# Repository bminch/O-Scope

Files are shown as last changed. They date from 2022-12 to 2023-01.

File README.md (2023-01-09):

# O-Scope
This repository contains the PCB design files, firmware, and software for the O-Scope, which is a low-cost (i.e., a cut-tape BoM cost of about $30 
as of fall 2020) two-channel oscilloscope / single-channel waveform generator up to a bandwidth of 200 kHz that fits into a solderless breadboard.  The oscilloscope's vertical resolution is 12 bits and each channel is sampled at 4 MS/s.  Each channel has a sample buffer of 1,500 points.  The 
oscilloscope probes are differential and have an equivalent input impedance of 1 MΩ || 15 pF with two input voltage ranges: ±10V and ±2V.  The 
waveform generator is capable of producing DC, sinusoidal, square, and triangle waves with an adjustable offset in the range of 0 - 5V. For an overview 
and demonstration of the O-Scope, see https://youtu.be/0cz0oYtfNsY.

I designed this instrument during the summer of 2020 based on a prior prototype, which I had made during the summers of 2016 and 2017, in order to support 
a remote / hybrid offering of ENGR 1125: Introduction to Sensors, Instrumentation, and Measurement at Olin College during the spring of 2021 in the midst 
of the COVID-19 pandemic.  During October and November 2020, I hand assembled and calibrated 90 O-Scopes at home, as shown in https://youtu.be/zYawotioLMc.  We used these instruments successfully during the spring 2021 and spring 2022 offerings of the course at Olin.

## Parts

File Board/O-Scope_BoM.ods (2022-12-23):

 |  | Number of boards = | 100 | Parts cost / board = | $28.34 |  |  |  |  |  |  |  |  |  |  |  |  |  |  |  |  |  |  | 0
Item | Qty | Reference(s) | Item Description | Manfacurer # | Digikey # (Cut Tape) | Digikey Product Page | Breakpoint | Price | Breakpoint | Price | Breakpoint | Price | Breakpoint | Price | Breakpoint | Price | Breakpoint | Price | Breakpoint | Price | Breakpoint | Price | Breakpoint | Price | Qty / Board | Total Qty | Unit Cost | Extended Cost | Cost / Board
1 | 3 | C1, C7, C8 | 0805, ±10%, X5R, 25-V, 10-µF ceramic capacitor | CC0805KKX5R8BB106 | 311-1869-1-ND | https://www.digikey.com/product-detail/en/yageo/CC0805KKX5R8BB106/311-1869-1-ND/5195771 | 1 | $0.50 | 10 | $0.35 | 100 | $0.23 | 500 | $0.17 | 1000 | $0.15 |  |  |  |  |  |  |  |  | 3 | 300 | $0.23 | $69.24 | $0.69
2 | 16 | C2, C3, C4, C5, C6, C9, C27, C28, C29, C30, C31, C34, C36, C37, C39, C40 | 0603, ±10%, X7R, 50-V, 0.1-µF ceramic capacitor | CL10B104JB8NNNC | 1276-1033-1-ND | https://www.digikey.com/product-detail/en/samsung-electro-mechanics/CL10B104JB8NNNC/1276-1033-1-ND/3889119 | 1 | $0.10 | 10 | $0.05 | 100 | $0.02 | 500 | $0.02 | 1000 | $0.01 |  |  |  |  |  |  |  |  | 16 | 1600 | $0.01 | $19.36 | $0.19
3 | 5 | C10, C19, C20, C21, C22 | 0603, ±1%, NP0, 50-V, 100-pF ceramic capacitor | 06035A101FAT2A | 478-6202-1-ND | https://www.digikey.com/product-detail/en/avx-corporation/06035A101FAT2A/478-6202-1-ND/2391401 | 1 | $0.21 | 10 | $0.14 | 100 | $0.07 | 500 | $0.05 | 1000 | $0.04 |  |  |  |  |  |  |  |  | 5 | 500 | $0.05 | $24.51 | $0.25
4 | 4 | C11, C12, C13, C14 | 0603, ±1%, NP0, 250-V, 15-pF ceramic capacitor | CBR06C150FAGAC | 399-8784-1-ND | http://www.digikey.com/product-detail/en/kemet/CBR06C150FAGAC/399-8784-1-ND/3479731 | 1 | $0.85 | 10 | $0.63 | 100 | $0.43 | 500 | $0.34 | 1000 | $0.29 |  |  |  |  |  |  |  |  | 4 | 400 | $0.43 | $171.36 | $1.71
5 | 4 | C15, C16, C17, C18 | 0603, ±1%, NP0, 50-V, 1-nF ceramic capacitor | GRM1885C1H102FA01D | 490-6376-1-ND | http://www.digikey.com/product-detail/en/murata-electronics-north-america/GRM1885C1H102FA01D/490-6376-1-ND/3845573 | 1 | $0.21 | 10 | $0.15 | 100 | $0.07 | 500 | $0.05 | 1000 | $0.04 |  |  |  |  |  |  |  |  | 4 | 400 | $0.07 | $27.52 | $0.28
6 | 4 | C23, C24, C25, C26 | SGC3S300NM 8.0 - 30-pF, 500-V trimmer capacitor | SGC3S300NM | 2447-SGC3S300NMCT-ND | https://www.digikey.com/product-detail/en/ew-electronics/SGC3S300NM/2447-SGC3S300NMCT-ND/11689325 | 1 | $0.96 | 10 | $0.84 | 25 | $0.79 | 50 | $0.76 | 100 | $0.73 | 250 | $0.66 | 500 | $0.59 |  |  |  |  | 4 | 400 | $0.66 | $264.00 | $2.64
7 | 1 | C35 | 0603, ±5%, X7R, 50-V, 10-nF ceramic capacitor | C0603C103J5RACTU | 399-1092-1-ND | https://www.digikey.com/product-search/en?keywords=399-1092-1-ND | 1 | $0.10 | 10 | $0.05 | 100 | $0.02 | 500 | $0.02 | 1000 | $0.01 |  |  |  |  |  |  |  |  | 1 | 100 | $0.02 | $2.36 | $0.02
8 | 1 | C38 | 0603, X7R, 25-V, 1-µF capacitor | CL10B105KA8NNNC | 1276-1184-1-ND | https://www.digikey.com/product-detail/en/samsung-electro-mechanics/CL10B105KA8NNNC/1276-1184-1-ND/3889270 | 1 | $0.10 | 10 | $0.05 | 100 | $0.02 | 500 | $0.02 | 1000 | $0.01 |  |  |  |  |  |  |  |  | 1 | 100 | $0.02 | $2.42 | $0.02
9 | 2 | D1, D4 | 0805 green LED | LTST-C170TGKT | 160-1887-1-ND | http://www.digikey.com/product-search/en?keywords=160-1887-1-ND | 1 | $0.59 | 10 | $0.43 | 100 | $0.28 | 500 | $0.20 | 1000 | $0.16 |  |  |  |  |  |  |  |  | 2 | 200 | $0.28 | $55.74 | $0.56
10 | 1 | D2 | 0805 red LED | LTST-C171KRKT | 160-1427-1-ND | http://www.digikey.com/product-search/en?keywords=160-1427-1-ND | 1 | $0.28 | 10 | $0.20 | 100 | $0.10 | 500 | $0.06 | 1000 | $0.05 |  |  |  |  |  |  |  |  | 1 | 100 | $0.10 | $9.68 | $0.10
11 | 1 | D3 | 0805 blue LED | LTST-C170TBKT | 160-1579-1-ND | http://www.digikey.com/product-search/en?keywords=160-1579-1-ND | 1 | $0.39 | 10 | $0.28 | 100 | $0.16 | 500 | $0.11 | 1000 | $0.09 |  |  |  |  |  |  |  |  | 1 | 100 | $0.16 | $16.07 | $0.16
12 | 1 | J2 | USB micro-B connector, SMT, right angle, horizontal | 2040002-1 | A108263CT-ND | http://www.digikey.com/product-detail/en/te-connectivity-amp-connectors/2040002-1/A108263CT-ND/4021990 | 1 | $2.23 | 10 | $2.03 | 25 | $1.90 | 50 | $1.82 | 100 | $1.74 | 250 | $1.57 | 500 | $1.45 |  |  |  |  | 1 | 100 | $1.74 | $173.71 | $1.74
13 | 2 | J3, J4 | 1x06, 0.1-in vertical male pin header | PBC36SAAN | S1011E-36-ND | https://www.digikey.com/product-detail/en/sullins-connector-solutions/PBC36SAAN/S1011E-36-ND/859621 | 1 | $2.10 | 10 | $1.88 | 100 | $1.55 | 500 | $1.23 | 1000 | $1.07 |  |  |  |  |  |  |  |  | 0.33 | 34 | $1.88 | $63.99 | $0.64
14 | 2 | J5, J6 | 1x02, 0.1-in vertical male pin header | PBC36SAAN | S1011E-36-ND | https://www.digikey.com/product-detail/en/sullins-connector-solutions/PBC36SAAN/S1011E-36-ND/859621 | 1 | $2.10 | 10 | $1.88 | 100 | $1.55 | 500 | $1.23 | 1000 | $1.07 |  |  |  |  |  |  |  |  | 0.11 | 12 | $1.88 | $22.58 | $0.23
15 | 4 | R1, R2, R37, R39 | 0603, ±1%, ±100ppm/Cº, 1/10-W, 10-kΩ resistor | RC0603FR-0710KL | 311-10.0KHRCT-ND | https://www.digikey.com/product-search/en?keywords=311-10.0KHRCT-ND | 1 | $0.10 | 10 | $0.02 | 100 | $0.01 | 1000 | $0.00 | 2500 | $0.00 |  |  |  |  |  |  |  |  | 4 | 400 | $0.01 | $3.76 | $0.04
16 | 4 | R4, R5, R6, R7 | 0603, ±1%, ±100ppm/Cº, 1/10-W, 1-kΩ resistor | RC0603FR-071KL | 311-1.00KHRCT-ND | http://www.digikey.com/product-search/en?keywords=311-1.00KHRCT-ND | 1 | $0.10 | 10 | $0.02 | 100 | $0.01 | 1000 | $0.00 | 2500 | $0.00 |  |  |  |  |  |  |  |  | 4 | 400 | $0.01 | $3.76 | $0.04
17 | 2 | R26, R28 | 0603, ±1%, ±100ppm/ºC, 1/10-W, 806-Ω resistor | RC0603FR-07806RL | 311-806HRCT-ND | https://www.digikey.com/products/en?keywords=311-806HRCT-ND | 1 | $0.10 | 10 | $0.02 | 100 | $0.01 | 1000 | $0.00 | 2500 | $0.00 |  |  |  |  |  |  |  |  | 2 | 200 | $0.01 | $1.88 | $0.02
18 | 4 | R8, R9, R10, R11 | 0805, ±1%, ±100ppm/ºC, 1/8-W, 887-kΩ resistor | CRCW0805887KFKEA | 541-887KCCT-ND | https://www.digikey.com/products/en?keywords=541-887KCCT-ND | 1 | $0.10 | 10 | $0.06 | 100 | $0.03 | 1000 | $0.01 | 2500 | $0.01 |  |  |  |  |  |  |  |  | 4 | 400 | $0.03 | $10.16 | $0.10
19 | 10 | R12, R13, R14, R15, R16, R21, R46, R47, R49, R50 | 0603, ±1%, ±100ppm/ºC, 1/10-W, 13-kΩ resistor | RC0603FR-0713KL | 311-13.0KHRCT-ND | https://www.digikey.com/products/en?keywords=311-13.0KHRCT-ND | 1 | $0.10 | 10 | $0.02 | 100 | $0.01 | 1000 | $0.00 | 2500 | $0.00 |  |  |  |  |  |  |  |  | 10 | 1000 | $0.00 | $4.21 | $0.04
20 | 8 | R17, R18, R19, R20, R22, R23, R24, R25 | 0603, ±1%, ±100ppm/ºC, 1/10-W, 200-kΩ resistor | RC0603FR-07200KL | 311-200KHRCT-ND | https://www.digikey.com/products/en?keywords=311-200KHRCT-ND | 1 | $0.10 | 10 | $0.02 | 100 | $0.01 | 1000 | $0.00 | 2500 | $0.00 |  |  |  |  |  |  |  |  | 8 | 800 | $0.01 | $7.52 | $0.08
21 | 4 | R27, R29, R44, R52 | 0603, ±1%, ±100ppm/Cº, 1/10-W, 200-Ω resistor | RC0603FR-07200RL | 311-200HRCT-ND | https://www.digikey.com/products/en?keywords=311-200HRCT-ND | 1 | $0.10 | 10 | $0.02 | 100 | $0.01 | 1000 | $0.00 | 2500 | $0.00 |  |  |  |  |  |  |  |  | 4 | 400 | $0.01 | $3.76 | $0.04
22 | 2 | R30, R31 | 0603, ±1%, ±100ppm/Cº, 1/10-W, 110-kΩ resistor | RC0603FR-07110KL | 311-110KHRCT-ND | https://www.digikey.com/products/en?keywords=311-110KHRCT-ND | 1 | $0.10 | 10 | $0.02 | 100 | $0.01 | 1000 | $0.00 | 2500 | $0.00 |  |  |  |  |  |  |  |  | 2 | 200 | $0.01 | $1.88 | $0.02
23 | 2 | R34, R42 | 0603, ±1%, ±100ppm/Cº, 1/10-W, 732-Ω resistor | RC0603FR-07732RL | 311-732HRCT-ND | https://www.digikey.com/products/en?keywords=311-732HRCT-ND | 1 | $0.10 | 10 | $0.02 | 100 | $0.01 | 1000 | $0.00 | 2500 | $0.00 |  |  |  |  |  |  |  |  | 2 | 200 | $0.01 | $1.88 | $0.02
24 | 4 | R35, R40, R45, R51 | 0603, ±1%, ±100ppm/Cº, 1/10-W, 301-Ω resistor | RC0603FR-07301RL | 311-301HRCT-ND | https://www.digikey.com/products/en?keywords=311-301HRCT-ND | 1 | $0.10 | 10 | $0.02 | 100 | $0.01 | 1000 | $0.00 | 2500 | $0.00 |  |  |  |  |  |  |  |  | 4 | 400 | $0.01 | $3.76 | $0.04
25 | 1 | R36 | 0603, ±1%, ±100ppm/ºC, 1/6-W, 18.2-Ω resistor | RC0603FR-0718R2L | 311-18.2HRCT-ND | https://www.digikey.com/products/en?keywords=311-18.2HRCT-ND | 1 | $0.10 | 10 | $0.02 | 100 | $0.01 | 1000 | $0.00 | 2500 | $0.00 |  |  |  |  |  |  |  |  | 1 | 100 | $0.01 | $0.94 | $0.01
26 | 1 | R38 | 0603, ±1%, ±100ppm/Cº, 1/10-W, 11.8-kΩ resistor | RC0603FR-0711K8L | 311-11.8KHRCT-ND | https://www.digikey.com/product-detail/en/yageo/RC0603FR-0711K8L/311-11.8KHRCT-ND/729850 | 1 | $0.10 | 10 | $0.02 | 100 | $0.01 | 1000 | $0.00 | 2500 | $0.00 |  |  |  |  |  |  |  |  | 1 | 100 | $0.01 | $0.94 | $0.01
27 | 4 | R3, R41, R48, R53 | 0603, ±1%, ±100ppm/Cº, 1/10-W, 90.9-kΩ resistor | RC0603FR-0790K9L | 311-90.9KHRCT-ND | https://www.digikey.com/products/en?keywords=311-90.9KHRCT-ND | 1 | $0.10 | 10 | $0.02 | 100 | $0.01 | 1000 | $0.00 | 2500 | $0.00 |  |  |  |  |  |  |  |  | 4 | 400 | $0.01 | $3.76 | $0.04
28 | 1 | R43 | 0603, ±1%, ±100ppm/Cº, 1/10-W, 66.5-kΩ resistor | RC0603FR-0766K5L | 311-66.5KHRCT-ND | https://www.digikey.com/product-detail/en/yageo/RC0603FR-0766K5L/311-66.5KHRCT-ND/730295 | 1 | $0.10 | 10 | $0.02 | 100 | $0.01 | 1000 | $0.00 | 2500 | $0.00 |  |  |  |  |  |  |  |  | 1 | 100 | $0.01 | $0.94 | $0.01
29 | 2 | S1, S2 | B3U-1000P tactile switch SPST-NO, top actuated, SMT | B3U-1000P | SW1020CT-ND | https://www.digikey.com/product-detail/en/omron-electronics-inc-emc-div/B3U-1000P/SW1020CT-ND/1534357 | 1 | $0.98 | 10 | $0.94 | 25 | $0.88 | 100 | $0.77 | 250 | $0.70 | 500 | $0.65 | 1000 | $0.60 |  |  |  |  | 2 | 200 | $0.77 | $153.00 | $1.53
30 | 1 | U1 | MCP1702 3.3-V, 250-mA, LDO linear regulator, SOT-23-3 | MCP1702T-3302E/CB | MCP1702T-3302E/CBCT-ND | http://www.digikey.com/product-search/en?keywords=MCP1702T-3302E%2FCBCT-ND | 1 | $0.48 | 25 | $0.40 | 100 | $0.36 |  |  |  |  |  |  |  |  |  |  |  |  | 1 | 100 | $0.36 | $36.00 | $0.36
31 | 1 | U2 | PIC24FJ128GC006 16-bit microcontroller, 64-TQFP | PIC24FJ128GC006-I/PT | PIC24FJ128GC006-I/PT-ND | https://www.digikey.com/product-detail/en/microchip-technology/PIC24FJ128GC006-I-PT/PIC24FJ128GC006-I-PT-ND/3872796 | 1 | $4.86 | 25 | $4.45 | 100 | $4.03 |  |  |  |  |  |  |  |  |  |  |  |  | 1 | 100 | $4.03 | $403.00 | $4.03
32 | 1 | U3 | MCP1501 ±0.1%, ±20-mA, 2.048-V reference, SOT-23-6 | MCP1501T-20E/CHY | MCP1501T-20E/CHYCT-ND | https://www.digikey.com/product-detail/en/microchip-technology/MCP1501T-20E-CHY/MCP1501T-20E-CHYCT-ND/5844629 | 1 | $0.76 | 25 | $0.63 | 100 | $0.58 |  |  |  |  |  |  |  |  |  |  |  |  | 1 | 100 | $0.58 | $58.00 | $0.58
33 | 1 | U4 | MCP6021 single op amp, SOT-23-5 | MCP6021T-E/OT | MCP6021T-E/OTDKR-ND | https://www.digikey.com/product-detail/en/microchip-technology/MCP6021T-E-OT/MCP6021T-E-OTDKR-ND/1980007 | 1 | $0.99 | 25 | $0.83 | 100 | $0.75 |  |  |  |  |  |  |  |  |  |  |  |  | 1 | 100 | $0.75 | $75.00 | $0.75
34 | 2 | U5, U6 | MCP6N11 instrumentation amplifier, 8-SOIC | MCP6N11-001E/SN | MCP6N11-001E/SN-ND | https://www.digikey.com/product-detail/en/microchip-technology/MCP6N11-001E-SN/MCP6N11-001E-SN-ND/2802054 | 1 | $1.35 | 25 | $1.13 | 100 | $1.02 |  |  |  |  |  |  |  |  |  |  |  |  | 2 | 200 | $1.02 | $204.00 | $2.04
35 | 2 | U7, U13 | MCP6024 quad op amp, 14-TSSOP | MCP6024-E/ST | MCP6024-E/ST-ND | https://www.digikey.com/product-detail/en/microchip-technology/MCP6024-E-ST/MCP6024-E-ST-ND/683231 | 1 | $1.91 | 25 | $1.59 | 100 | $1.44 |  |  |  |  |  |  |  |  |  |  |  |  | 2 | 200 | $1.44 | $288.00 | $2.88
36 | 2 | U8, U10 | CD74HC4053 triple 2:1 multiplexer, 16-TSSOP | CD74HC4053PWR | 296-12111-1-ND | https://www.digikey.com/product-detail/en/texas-instruments/CD74HC4053PWR/296-12111-1-ND/404448 | 1 | $0.46 | 10 | $0.38 | 25 | $0.34 | 100 | $0.26 | 250 | $0.23 | 500 | $0.19 | 1000 | $0.14 |  |  |  |  | 2 | 200 | $0.26 | $51.20 | $0.51
37 | 1 | U9 | AD9837 DDS waveform generator, 10LFCSP | AD9837ACPZ-RL7 | AD9837ACPZ-RL7CT-ND | https://www.digikey.com/product-detail/en/analog-devices-inc/AD9837ACPZ-RL7/AD9837ACPZ-RL7CT-ND/2677455 | 1 | $4.37 | 10 | $3.93 | 25 | $3.71 | 100 | $3.22 | 250 | $3.05 | 500 | $2.74 |  |  |  |  |  |  | 1 | 100 | $3.22 | $321.75 | $3.22
38 | 1 | U11 | TLE2426D rail splitter 20V, ±1%, 8-SOIC | TLE2426IDR | 296-1345-1-ND | https://www.digikey.com/product-detail/en/texas-instruments/TLE2426IDR/296-1345-1-ND/404963 | 1 | $2.07 | 10 | $1.86 | 25 | $1.76 | 100 | $1.41 | 250 | $1.23 | 500 | $1.20 | 1000 | $0.95 |  |  |  |  | 1 | 100 | $1.41 | $140.60 | $1.41
39 | 1 | U12 | AD5160 5kΩ SPI digital potentiometer, SOT-23-8 | AD5160BRJZ5-RL7 | AD5160BRJZ5-RL7CT-ND | https://www.digikey.com/product-detail/en/analog-devices-inc/AD5160BRJZ5-RL7/AD5160BRJZ5-RL7CT-ND/1718628 | 1 | $1.95 | 10 | $1.75 | 25 | $1.65 | 100 | $1.32 | 250 | $1.16 | 500 | $1.12 | 1000 | $0.96 |  |  |  |  | 1 | 100 | $1.32 | $132.00 | $1.32

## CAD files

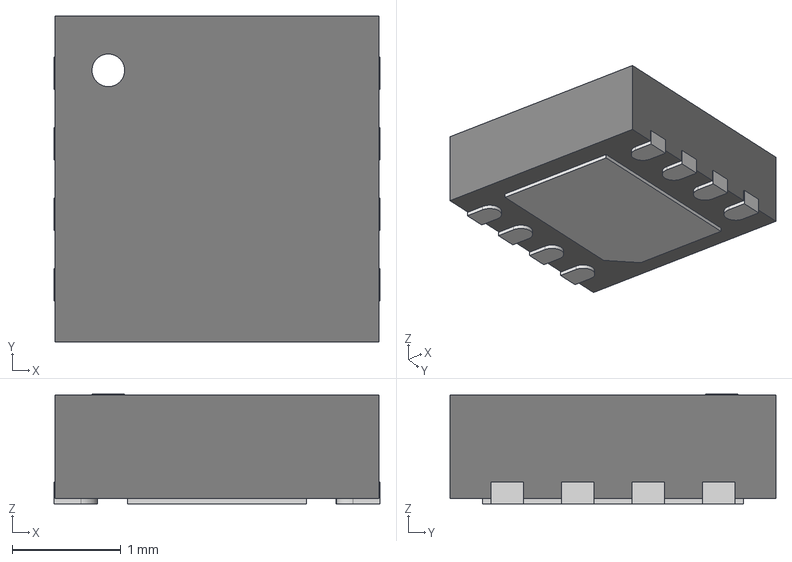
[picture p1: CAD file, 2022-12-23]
Board/KiCad/Eclectronics/3dshapes/DFN8_3x3_0.65.step
3.00 x 3.00 x 1.01 mm

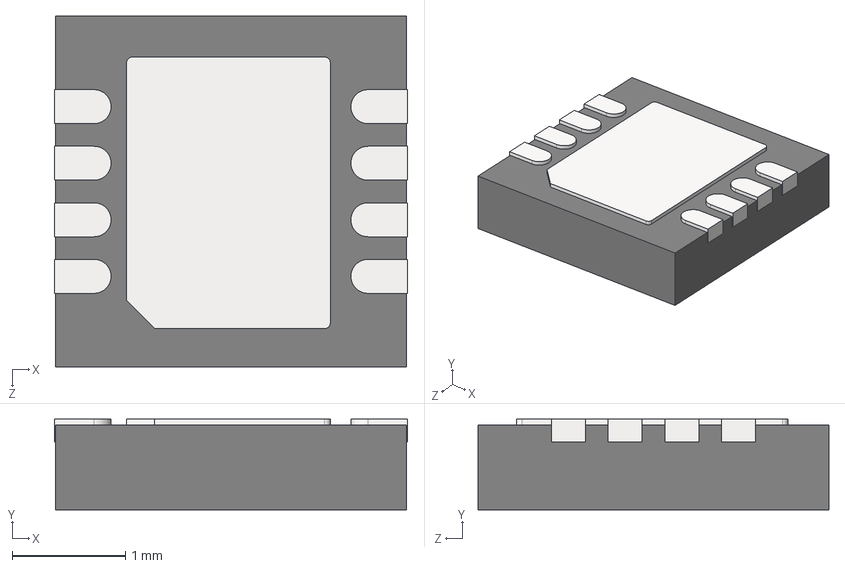
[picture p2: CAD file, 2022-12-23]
Board/KiCad/Eclectronics/3dshapes/DFN-8-3x3-0_5.STEP
3.12 x 0.8 x 3.10 mm
User Library-My-DFN-8-3x3-0.5_Part 11
User Library-My-DFN-8-3x3-0.5_Body
User Library-My-DFN-8-3x3-0.5_14
User Library-My-DFN-8-3x3-0.5_13
User Library-My-DFN-8-3x3-0.5_2
User Library-My-DFN-8-3x3-0.5_1
User Library-My-DFN-8-3x3-0.5_11
User Library-My-DFN-8-3x3-0.5_3
User Library-My-DFN-8-3x3-0.5_12
User Library-My-DFN-8-3x3-0.5_4
User Library-My-DFN-8-3x3-0.5_TP

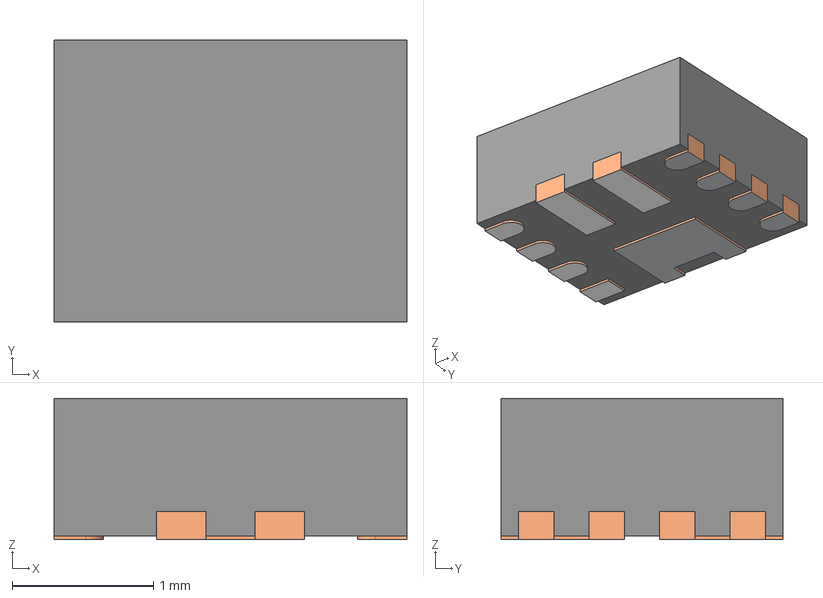
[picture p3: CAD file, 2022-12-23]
Board/KiCad/Eclectronics/3dshapes/RNR0011A.stp
2.50 x 2.00 x 1.00 mm
FRAME-RNR0011A
BODY-QFN
PIN1-ID

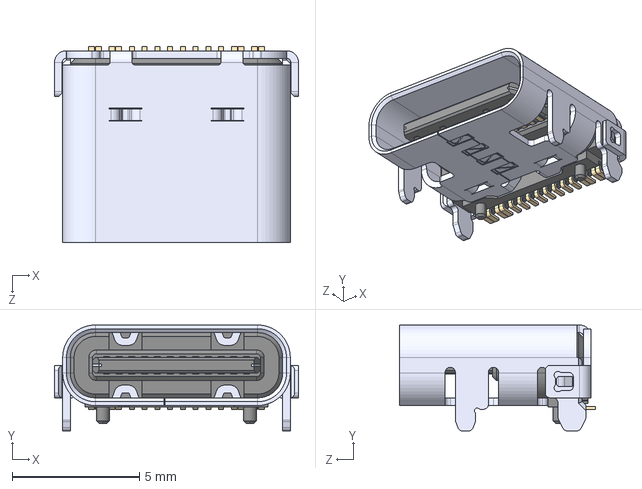
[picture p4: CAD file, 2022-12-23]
Board/KiCad/Eclectronics/3dshapes/USB4105-GF-A.step
9.58 x 4.16 x 7.71 mm

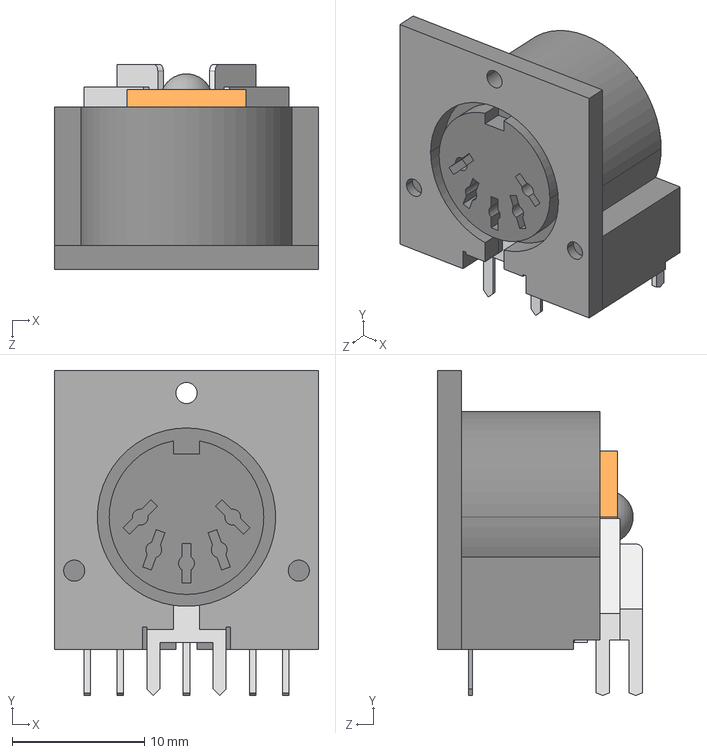
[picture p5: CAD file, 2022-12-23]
Board/KiCad/Eclectronics/3dshapes/CUI_SDS-50J.step
20.0 x 24.6 x 15.5 mm

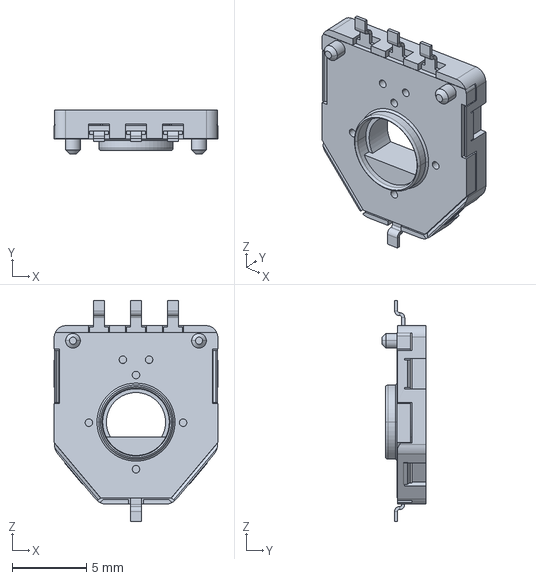
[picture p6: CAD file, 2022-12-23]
Board/KiCad/Eclectronics/3dshapes/3382g-001-xxx.stp
11.0 x 2.95 x 14.9 mm

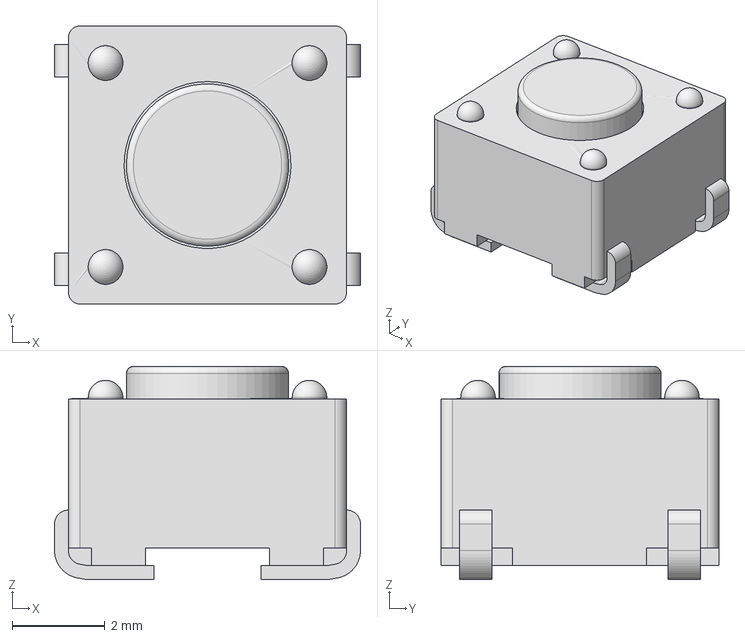
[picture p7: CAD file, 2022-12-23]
Board/KiCad/Eclectronics/3dshapes/TL3301NFxxxxJ.stp
6.60 x 6.00 x 4.60 mm

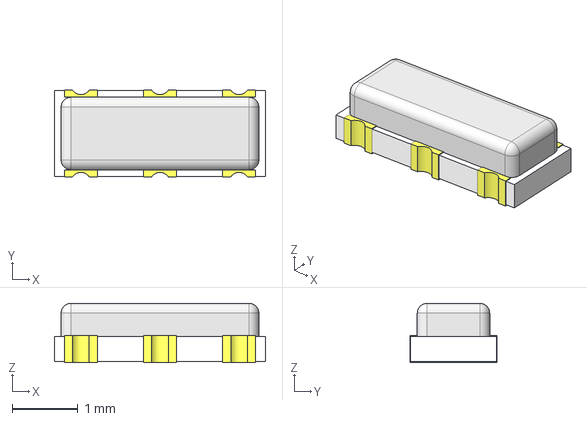
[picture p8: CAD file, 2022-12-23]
Board/KiCad/Eclectronics/3dshapes/CSTNE.step
3.20 x 1.32 x 0.9 mm

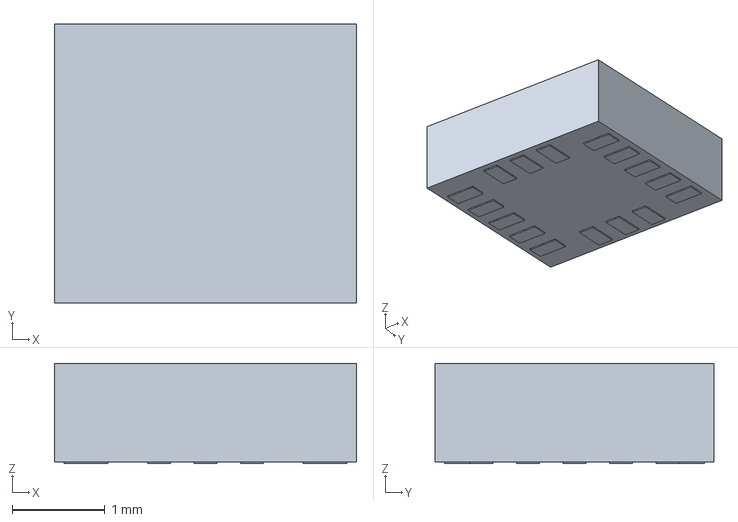
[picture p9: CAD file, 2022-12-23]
Board/KiCad/Eclectronics/3dshapes/Analog_Devices_Inc_-_ADXL362BCCZ.step
3.25 x 3.00 x 1.08 mm

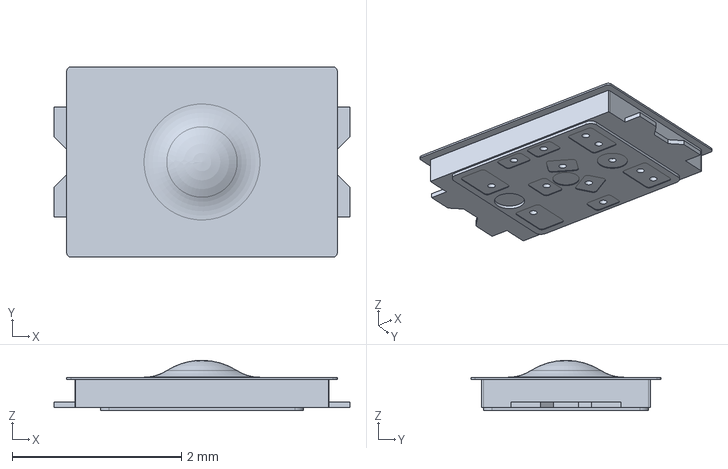
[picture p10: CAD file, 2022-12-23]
Board/KiCad/Eclectronics/3dshapes/KXT321LHS.stp
3.50 x 2.25 x 0.595 mm

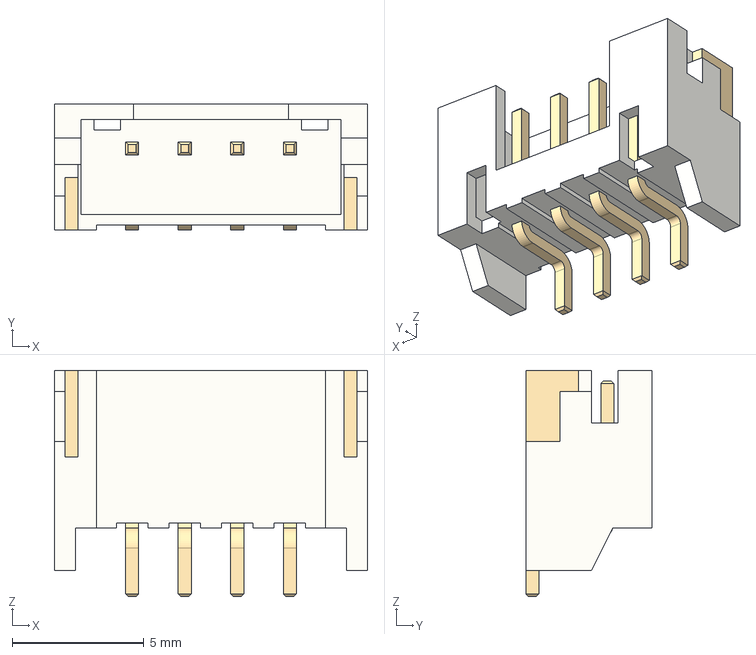
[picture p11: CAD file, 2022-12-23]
Board/KiCad/Eclectronics/3dshapes/S4B-PH-SM4-TB.stp
11.9 x 4.80 x 8.60 mm

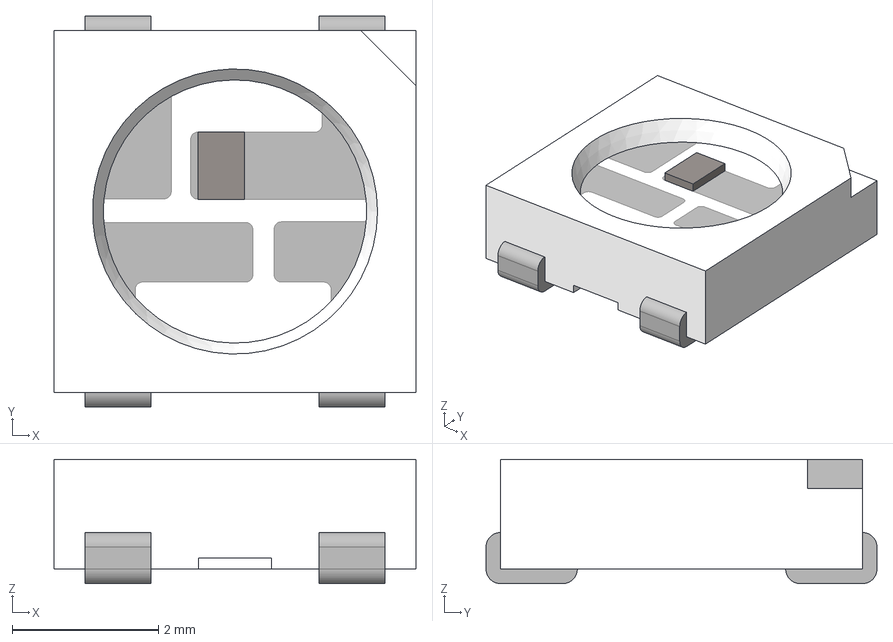
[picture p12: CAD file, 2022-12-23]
Board/KiCad/Eclectronics/3dshapes/WS2812_RGB_LED_updated.stp
4.95 x 5.35 x 1.70 mm

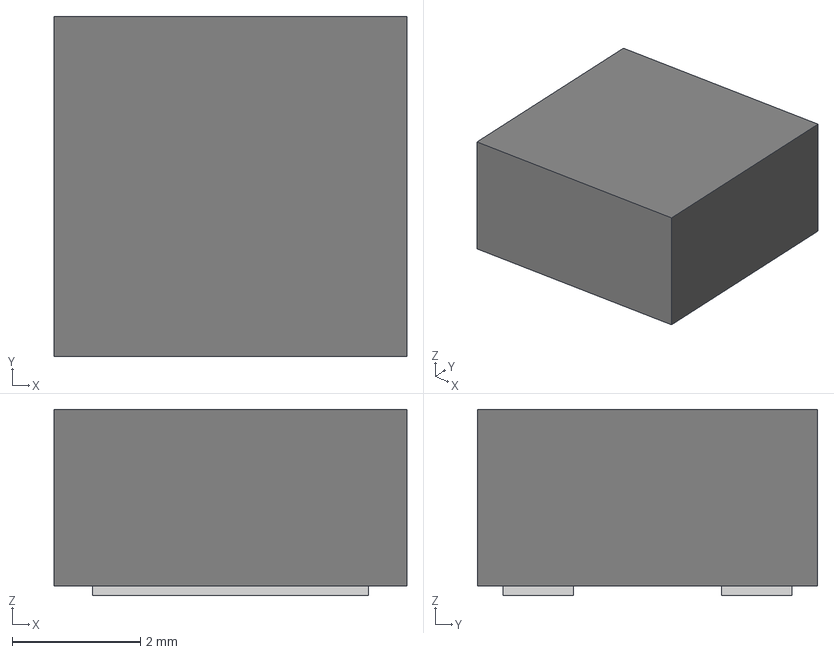
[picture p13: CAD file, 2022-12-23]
Board/KiCad/Eclectronics/3dshapes/PA5003.182NLT.step
5.50 x 5.30 x 2.90 mm

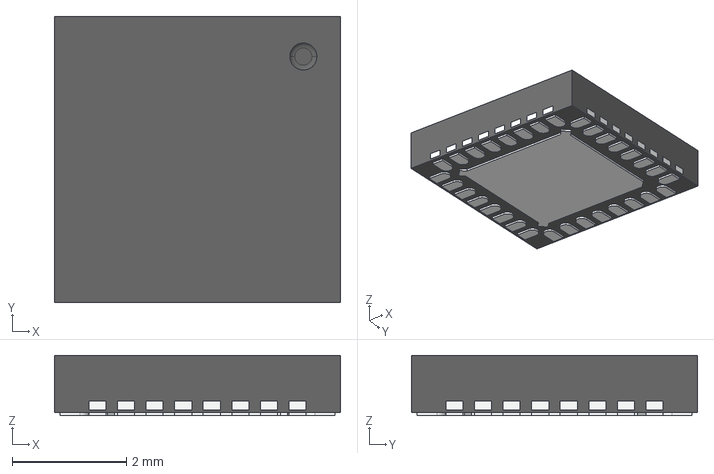
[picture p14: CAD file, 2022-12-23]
Board/KiCad/Eclectronics/3dshapes/QFN-32_5x5.stp
5.00 x 5.00 x 1.05 mm

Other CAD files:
Board/KiCad/Eclectronics/3dshapes/UFQFPN48.stp
Board/KiCad/Eclectronics/3dshapes/RP2040_QFN_PACKAGE.STEP
Board/KiCad/Eclectronics/3dshapes/WSON8-6x5.STEP
Board/KiCad/Eclectronics/3dshapes/ABM10.STP
Board/KiCad/Eclectronics/3dshapes/ABS06-107.STP
Board/KiCad/Eclectronics/3dshapes/SJ-3524-SMT-TR-BE.step
Board/KiCad/Eclectronics/3dshapes/WS2812-2020.STEP

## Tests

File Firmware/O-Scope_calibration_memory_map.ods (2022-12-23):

address | ch | num_avg | ch_range | wg_range | contents
0x10000 | 1 | 0 | 0 |  | int(round(16. * self.ch1_zero[num_avg][ch_range]))
0x10002 | 1 | 0 | 1 |  | int(round(16. * self.ch1_zero[num_avg][ch_range]))
0x10004 | 1 | 1 | 0 |  | int(round(16. * self.ch1_zero[num_avg][ch_range]))
0x10006 | 1 | 1 | 1 |  | int(round(16. * self.ch1_zero[num_avg][ch_range]))
0x10008 | 1 | 2 | 0 |  | int(round(16. * self.ch1_zero[num_avg][ch_range]))
0x1000A | 1 | 2 | 1 |  | int(round(16. * self.ch1_zero[num_avg][ch_range]))
0x1000C | 1 | 3 | 0 |  | int(round(16. * self.ch1_zero[num_avg][ch_range]))
0x1000E | 1 | 3 | 1 |  | int(round(16. * self.ch1_zero[num_avg][ch_range]))
0x10010 | 1 | 4 | 0 |  | int(round(16. * self.ch1_zero[num_avg][ch_range]))
0x10012 | 1 | 4 | 1 |  | int(round(16. * self.ch1_zero[num_avg][ch_range]))
0x10014 | 2 | 0 | 0 |  | int(round(16. * self.ch2_zero[num_avg][ch_range]))
0x10016 | 2 | 0 | 1 |  | int(round(16. * self.ch2_zero[num_avg][ch_range]))
0x10018 | 2 | 1 | 0 |  | int(round(16. * self.ch2_zero[num_avg][ch_range]))
0x1001A | 2 | 1 | 1 |  | int(round(16. * self.ch2_zero[num_avg][ch_range]))
0x1001C | 2 | 2 | 0 |  | int(round(16. * self.ch2_zero[num_avg][ch_range]))
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

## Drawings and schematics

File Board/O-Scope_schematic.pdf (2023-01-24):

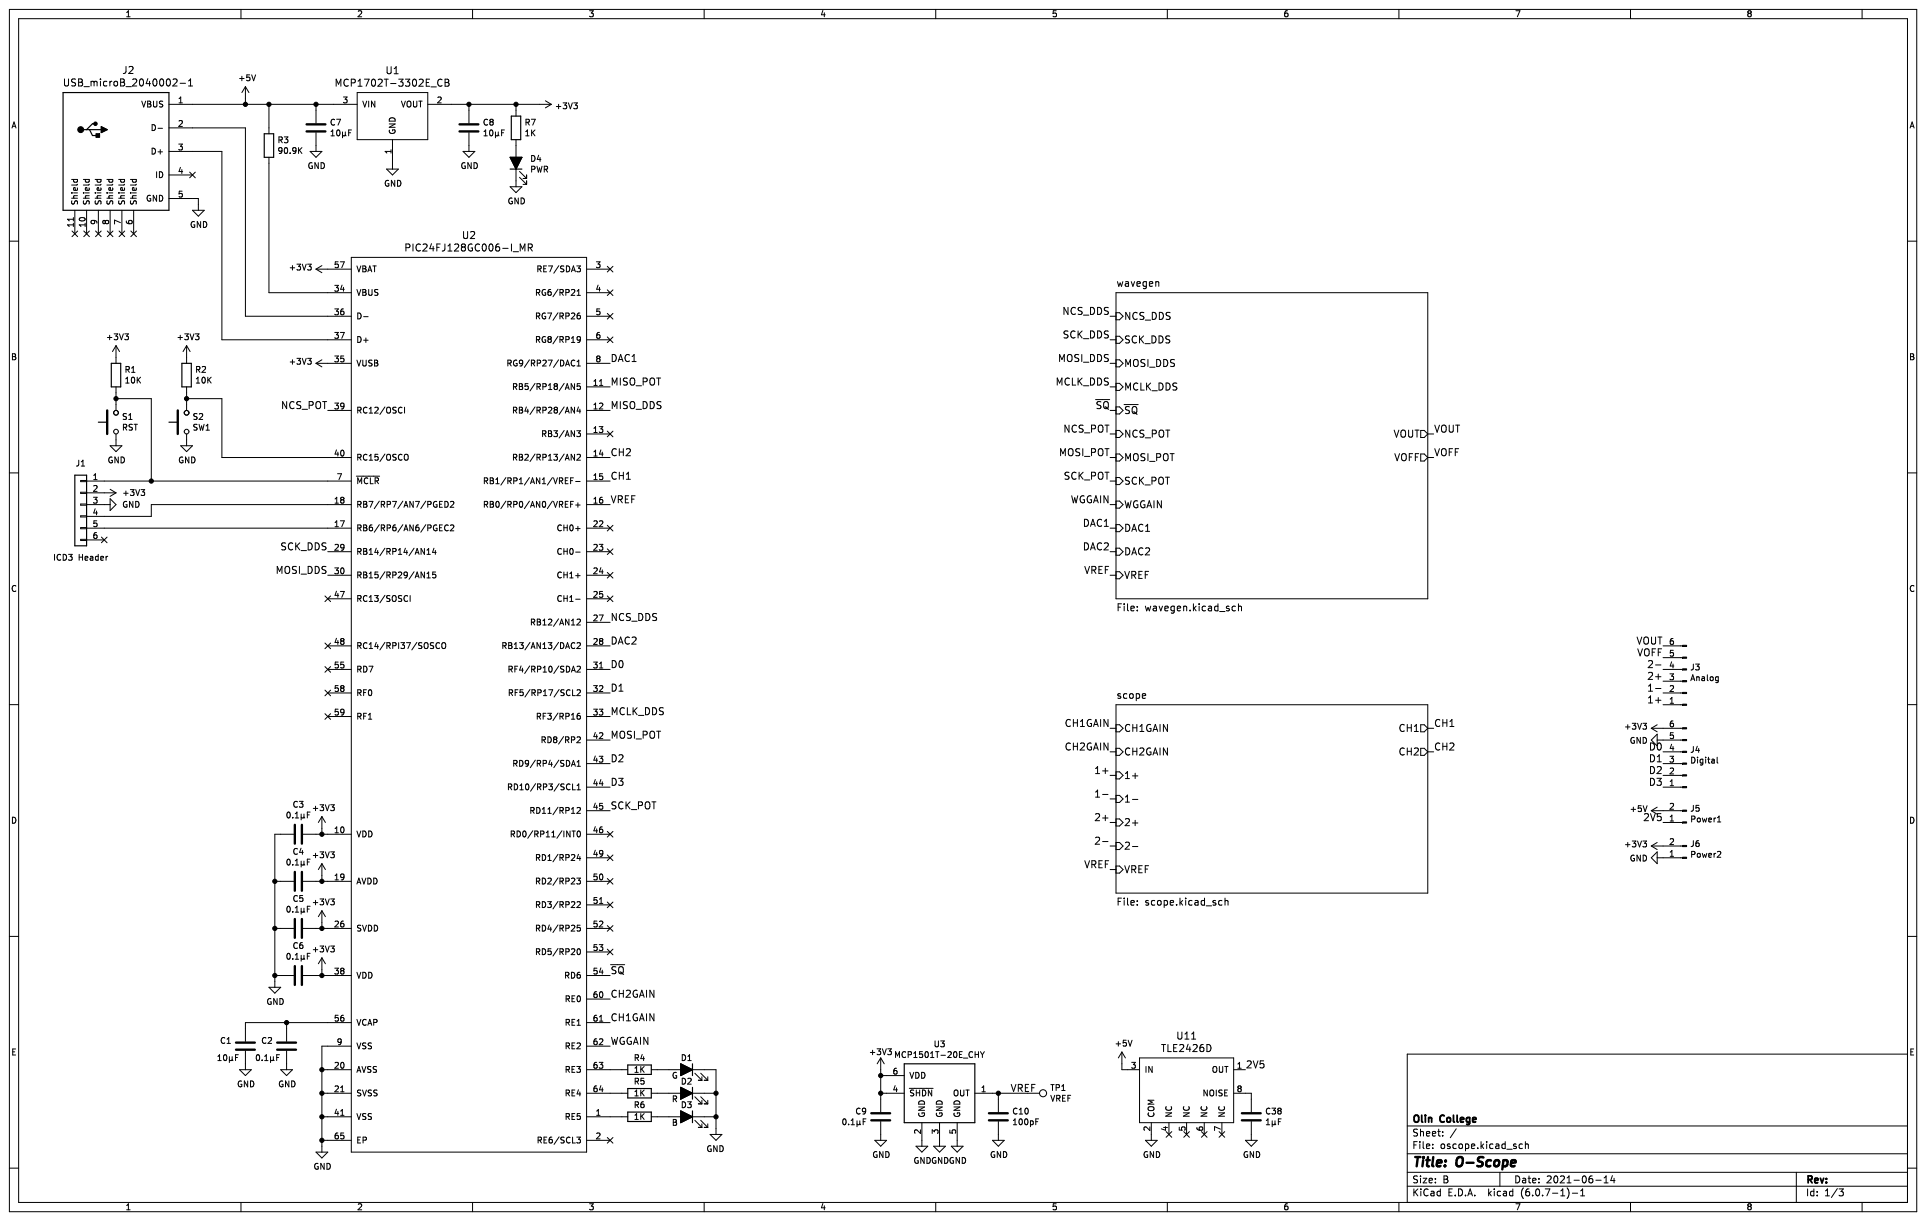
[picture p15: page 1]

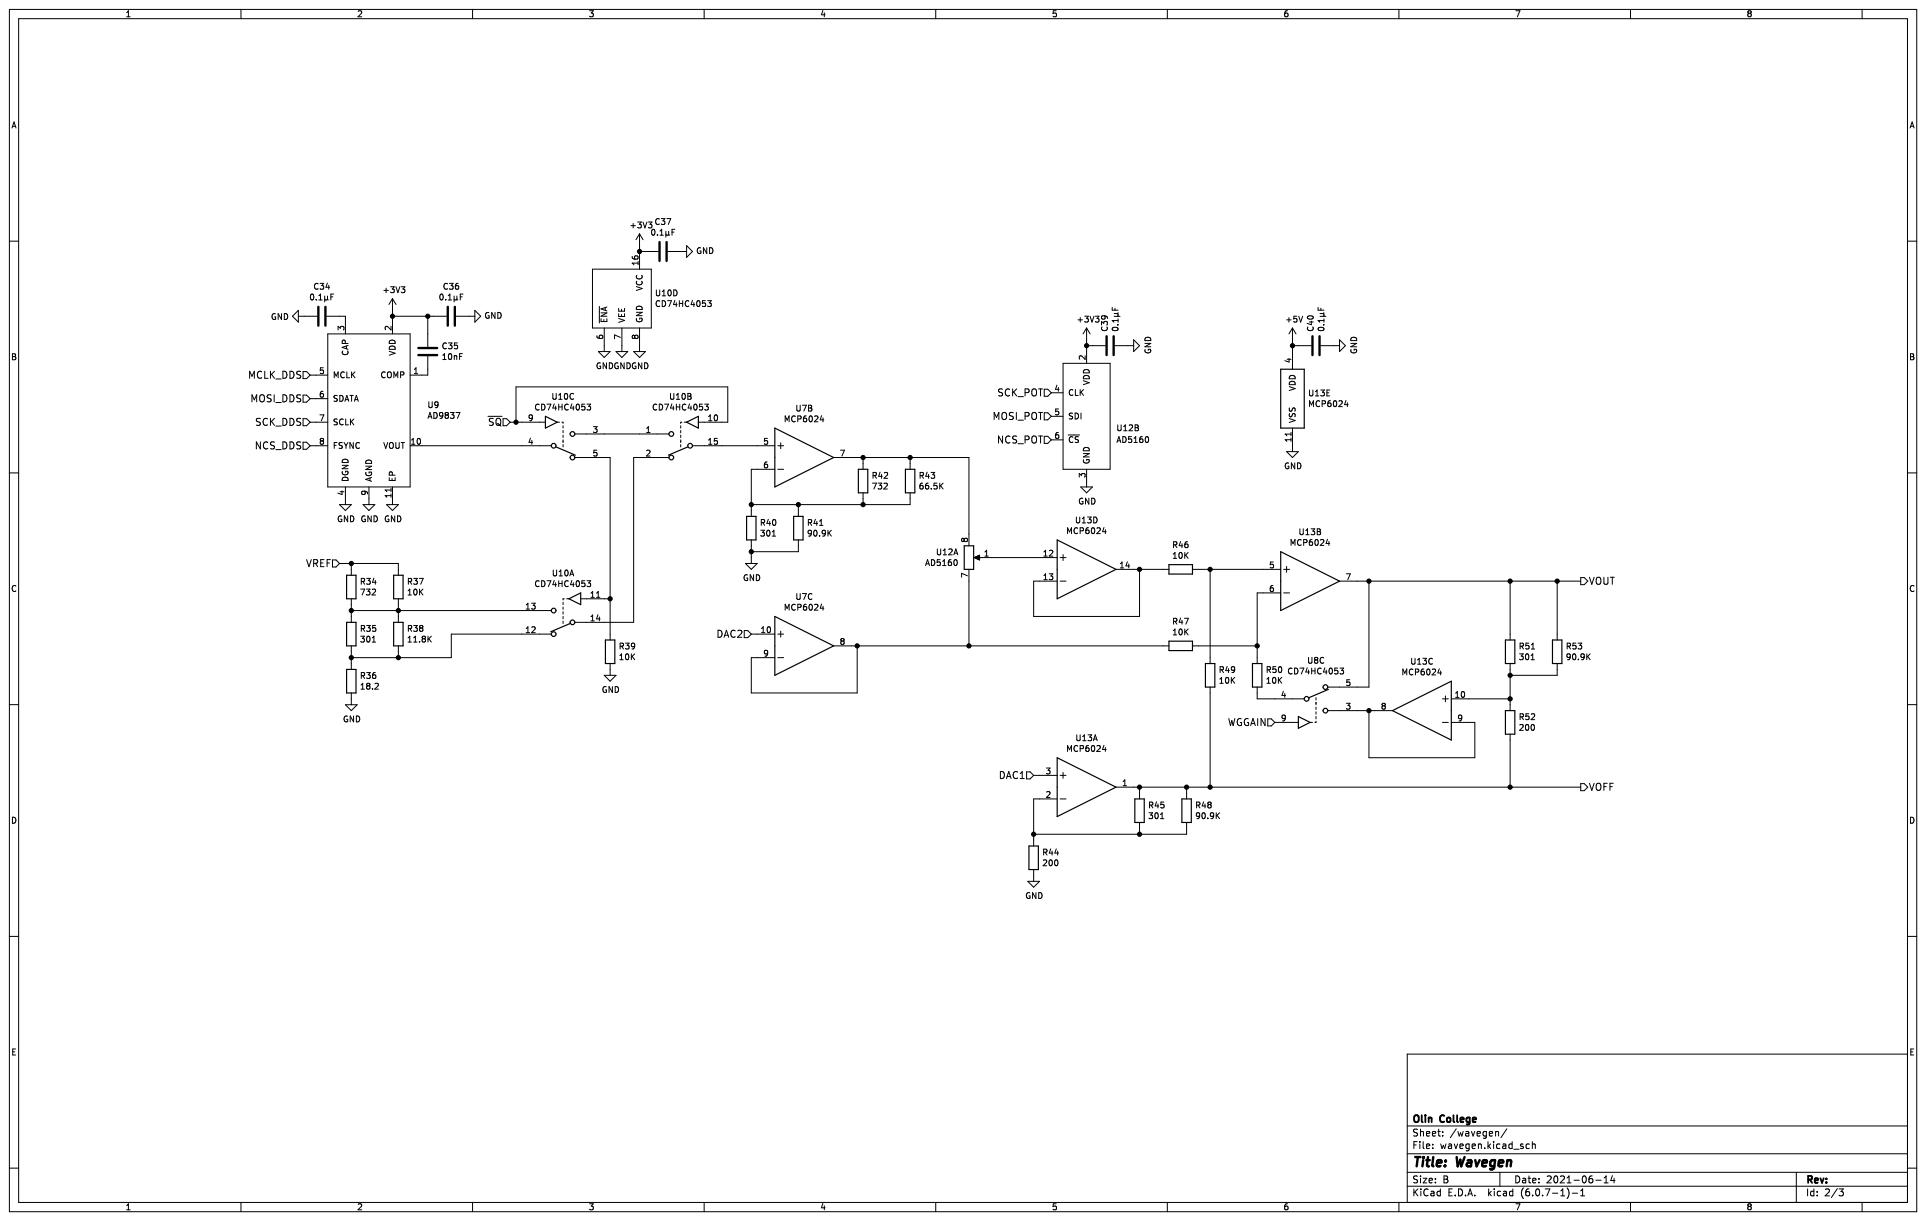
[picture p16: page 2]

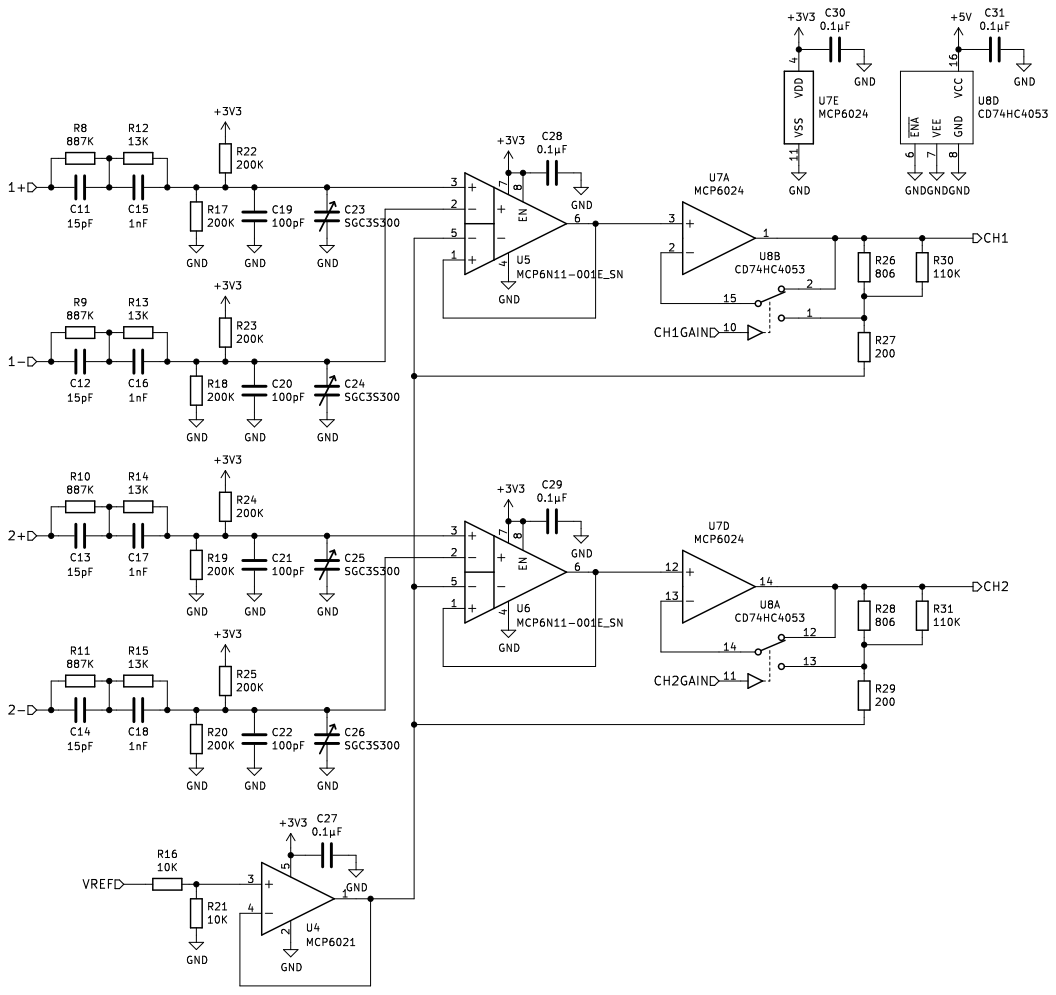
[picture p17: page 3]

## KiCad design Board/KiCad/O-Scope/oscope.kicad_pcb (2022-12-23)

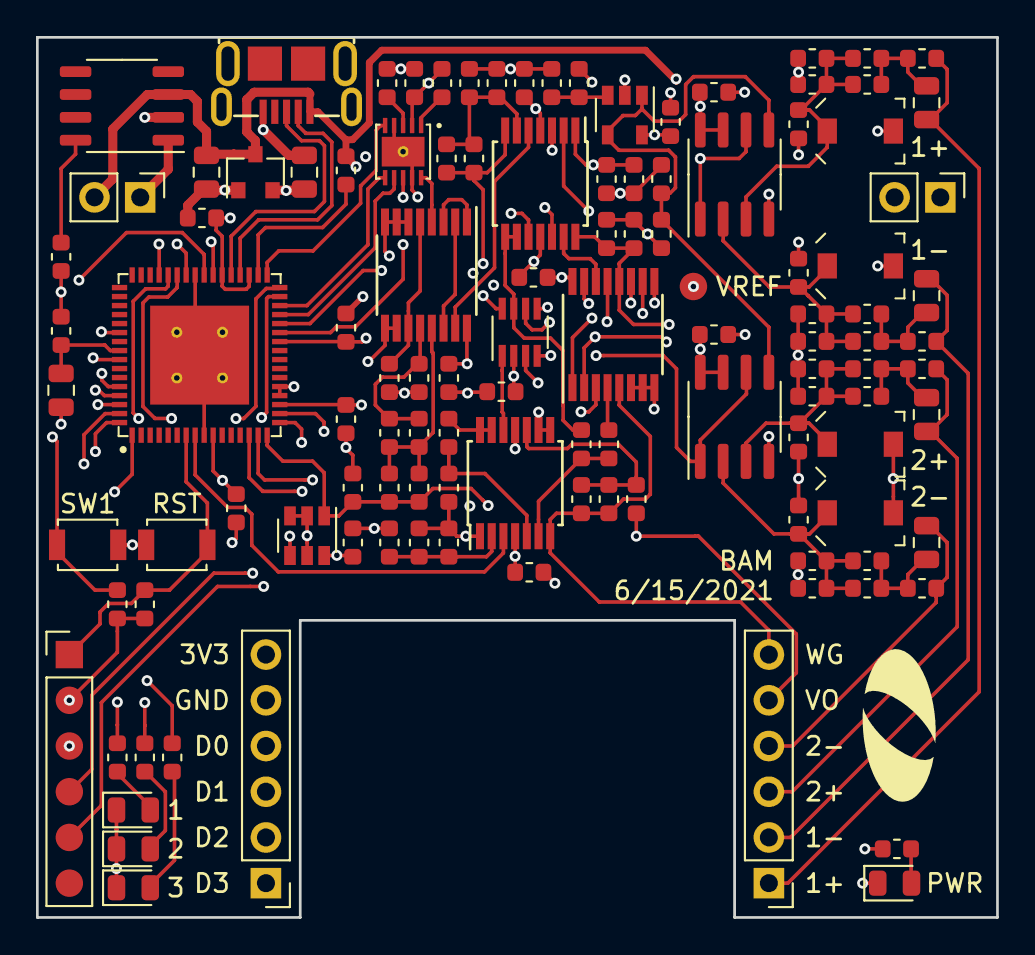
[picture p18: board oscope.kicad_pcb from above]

Board: 4 copper layers, 53.3 x 48.9 mm, 117 parts (1 on the bottom side), 82 nets.

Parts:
C1, C7, C8: 10µF; C_0805_2012Metric
C2, C3, C4, C5, C6, C9, C27, C28, C29, C30, C31, C34, C36, C37, C39, C40: 0.1µF; C_0603_1608Metric
C10, C19, C20, C21, C22: 100pF; C_0603_1608Metric
C11, C12, C13, C14: 15pF; C_0603_1608Metric
C15, C16, C17, C18: 1nF; C_0603_1608Metric
C23, C24, C25, C26: SGC3S300; C_Trimmer_Sprague-Goodman_SGC3
C35: 10nF; C_0603_1608Metric
C38: 1µF; C_0603_1608Metric
D1: G; LED_0805_2012Metric
D2: R; LED_0805_2012Metric
D3: B; LED_0805_2012Metric
D4: PWR; LED_0805_2012Metric
J1: ICD3 Header; ICD3_header
J2: USB_microB_2040002-1
J3: Analog; PinHeader_1x06_P2.54mm_Vertical
J4: Digital; PinHeader_1x06_P2.54mm_Vertical
J5: Power1; PinHeader_1x02_P2.54mm_Vertical
J6: Power2; PinHeader_1x02_P2.54mm_Vertical
OlinLogoLg1: G***; OlinLogoLg1
OlinLogoTruncated: G***; OlinLogoTruncated
R1, R2, R16, R21, R37, R39, R46, R47, R49, R50: 10K; R_0603_1608Metric
R3, R41, R48, R53: 90.9K; R_0603_1608Metric
R4, R5, R6, R7: 1K; R_0603_1608Metric
R8, R9, R10, R11: 8.87M; R_0805_2012Metric
R12, R13, R14, R15: 130K; R_0603_1608Metric
R17, R18, R19, R20, R22, R23, R24, R25: 2M; R_0603_1608Metric
R26, R28: 806; R_0603_1608Metric
R27, R29, R44, R52: 200; R_0603_1608Metric
R30, R31: 110K; R_0603_1608Metric
R34, R42: 732; R_0603_1608Metric
R35, R40, R45, R51: 301; R_0603_1608Metric
R36: 18.2; R_0603_1608Metric
R38: 11.8K; R_0603_1608Metric
R43: 66.5K; R_0603_1608Metric
S1: RST; SW_SPST_B3U-1000P
S2: SW1; SW_SPST_B3U-1000P
TP1: VREF; 60mil_testpoint
U1: MCP1702T-3302E_CB; SOT-23
U2: PIC24FJ128GC006-I_MR; pic24fj128gc006
U3: MCP1501T-20E_CHY; SOT-23-6
U4: MCP6021; SOT-23-5
U5, U6: MCP6N11-001E_SN; SOIC-8_3.9x4.9mm_P1.27mm
U7, U13: MCP6024; TSSOP-14_4.4x5mm_P0.65mm
U8, U10: CD74HC4053; TSSOP-16_4.4x5mm_P0.65mm
U9: AD9837
U11: TLE2426D; SO-8_3.9x4.9mm_P1.27mm
U12: AD5160; TSOT-23-8

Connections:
+3V3: C3.2, C4.2, C5.2, C6.2, C8.1, C9.1, C27.2, C28.2, C29.2, C30.2, C35.1, C36.2, C37.2, C39.1, J1.2, J4.6, J6.2, R1.1, R2.1, R7.1, R22.2, R23.2, R24.2, R25.2, U1.2, U2.10, U2.19, U2.26, U2.35, U2.38, U2.57, U3.4, U3.6, U4.5, U5.7, U5.8, U6.7, U6.8, U7.4, U9.2, U10.16, U12.2
+5V: C7.1, C31.2, C40.1, J2.1, J5.2, R3.1, U1.3, U8.16, U11.3, U13.4
/1+: C11.1, J3.1, R8.2
/1-: C12.1, J3.2, R9.2
/2+: C13.1, J3.3, R10.2
/2-: C14.1, J3.4, R11.2
/2V5: J5.1, U11.1
/CH1: R26.1, R30.1, U2.15, U7.1, U8.2
/CH1GAIN: U2.61, U8.10
/CH2: R28.1, R31.1, U2.14, U7.14, U8.12
/CH2GAIN: U2.60, U8.11
/D0: J4.4, U2.31
/D1: J4.3, U2.32
/D2: J4.2, U2.43
/D3: J4.1, U2.44
/DAC1: U2.8, U13.3
/DAC2: U2.28, U7.10
/MCLK_DDS: U2.33, U9.5
/MOSI_DDS: U2.30, U9.6
/MOSI_POT: U2.42, U12.5
/NCS_DDS: U2.27, U9.8
/NCS_POT: U2.39, U12.6
/SCK_DDS: U2.29, U9.7
/SCK_POT: U2.45, U12.4
/VOFF: J3.5, R45.1, R48.1, R49.1, R52.2, U13.1
/VOUT: J3.6, R51.1, R53.1, U8.5, U13.7
/VREF: C10.1, R16.2, R34.1, R37.1, TP1.1, U2.16, U3.1
/WGGAIN: U2.62, U8.9
/~SQ: U2.54, U10.9, U10.10
GND: C1.1, C2.1, C3.1, C4.1, C5.1, C6.1, C7.2, C8.2, C9.2, C10.2, C19.2, C20.2, C21.2, C22.2, C23.2, C24.2, C25.2, C26.2, C27.1, C28.1, C29.1, C30.1, C31.1, C34.2, C36.1, C37.1, C38.2, C39.2, C40.2, D1.1, D2.1, D3.1, D4.1, J1.3, J2.5, J4.5, J6.1, R17.1, R18.1, R19.1, R20.1, R21.1, R36.2, R39.1, R40.2, R41.2, R44.2, S1.1, S2.1, U1.1, U2.9, U2.20, U2.21, U2.41, U2.65, U3.2, U3.3, U3.5, U4.2, U5.4, U6.4, U7.11, U8.6, U8.7, U8.8, U9.4, U9.9, U9.11, U10.6, U10.7, U10.8, U11.2, U12.3, U13.11
unnamed: C1.2, C2.2, U2.56
unnamed: C11.2, C15.1, R8.1, R12.2
unnamed: C12.2, C16.1, R9.1, R13.2
unnamed: C13.2, C17.1, R10.1, R14.2
unnamed: C14.2, C18.1, R11.1, R15.2
unnamed: C15.2, C19.1, C23.1, R12.1, R17.2, R22.1, U5.3
unnamed: C16.2, C20.1, C24.1, R13.1, R18.2, R23.1, U5.2
unnamed: C17.2, C21.1, C25.1, R14.1, R19.2, R24.1, U6.3
unnamed: C18.2, C22.1, C26.1, R15.1, R20.2, R25.1, U6.2
unnamed: C34.1, U9.3
unnamed: C35.2, U9.1
unnamed: C38.1, U11.8
unnamed: D1.2, R4.2
unnamed: D2.2, R5.2
unnamed: D3.2, R6.2
unnamed: D4.2, R7.2
unnamed: J1.1, R1.2, S1.2, U2.7
unnamed: J1.4, U2.18
unnamed: J1.5, U2.17
unnamed: J2.2, U2.36
unnamed: J2.3, U2.37
unnamed: R2.2, S2.2, U2.40
unnamed: R3.2, U2.34
unnamed: R4.1, U2.63
unnamed: R5.1, U2.64
unnamed: R6.1, U2.1
unnamed: R16.1, R21.2, U4.3
unnamed: R26.2, R27.1, R30.2, U8.1
unnamed: R27.2, R29.2, U4.1, U4.4, U5.5, U6.5
unnamed: R28.2, R29.1, R31.2, U8.13
unnamed: R34.2, R35.1, R37.2, R38.1, U10.13
unnamed: R35.2, R36.1, R38.2, U10.12
unnamed: R39.2, U10.5, U10.11
unnamed: R40.1, R41.1, R42.2, R43.2, U7.6
unnamed: R42.1, R43.1, U7.7, U12.8
unnamed: R44.1, R45.2, R48.2, U13.2
unnamed: R46.1, R49.2, U13.5
unnamed: R46.2, U13.13, U13.14
unnamed: R47.1, R50.2, U13.6
unnamed: R47.2, U7.8, U7.9, U12.7
unnamed: R50.1, U8.4
unnamed: R51.2, R52.1, R53.2, U13.10
unnamed: U5.1, U5.6, U7.3
unnamed: U6.1, U6.6, U7.12
unnamed: U7.2, U8.15
unnamed: U7.13, U8.14
unnamed: U10.1, U10.3
unnamed: U9.10, U10.4
unnamed: U10.2, U10.14
unnamed: U7.5, U10.15
unnamed: U12.1, U13.12
unnamed: U8.3, U13.8, U13.9

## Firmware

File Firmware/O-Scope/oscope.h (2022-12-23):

#ifndef _OSCOPE_H_
#define _OSCOPE_H_

#include "pic24fj.h"
#include "common.h"
#include <stdint.h>

// LED pin definitions
#define LED1                LATEbits.LATE3
#define LED2                LATEbits.LATE4
#define LED3                LATEbits.LATE5

#define LED1_DIR            TRISEbits.TRISE3
#define LED2_DIR            TRISEbits.TRISE4
#define LED3_DIR            TRISEbits.TRISE5

// Tactile switch pin definitions
#define SW1                 PORTCbits.RC15

#define SW1_DIR             TRISCbits.TRISC15

// Digital header pin definitions
#define D0                  PORTFbits.RF4
#define D1                  PORTFbits.RF5
#define D2                  PORTDbits.RD9
#define D3                  PORTDbits.RD10

#define D0_DIR              TRISFbits.TRISF4
#define D1_DIR              TRISFbits.TRISF5
#define D2_DIR              TRISDbits.TRISD9
#define D3_DIR              TRISDbits.TRISD10

#define D0_LAT              LATFbits.LATF4
#define D1_LAT              LATFbits.LATF5
#define D2_LAT              LATDbits.LATD9
#define D3_LAT              LATDbits.LATD10

#define D0_RP               10
#define D1_RP               17
#define D2_RP               4
#define D3_RP               3

#define D0_OD               ODCFbits.ODF4
#define D1_OD               ODCFbits.ODF5
#define D2_OD               ODCDbits.ODD9
#define D3_OD               ODCDbits.ODD10

#define D0_PU               CNPU2bits.CN17PUE
#define D1_PU               CNPU2bits.CN18PUE
#define D2_PU               CNPU4bits.CN54PUE
#define D3_PU               CNPU4bits.CN55PUE

#define D0_PD               CNPD2bits.CN17PDE
#define D1_PD               CNPD2bits.CN18PDE
#define D2_PD               CNPD4bits.CN54PDE
#define D3_PD               CNPD4bits.CN55PDE

// AD9837 DDS interface pin defintions
#define nCS_DDS             LATBbits.LATB12
#define SCK_DDS             PORTBbits.RB14
#define MOSI_DDS            PORTBbits.RB15
#define MISO_DDS            PORTBbits.RB4
#define MCLK_DDS            PORTFbits.RF3

#define nCS_DDS_DIR         TRISBbits.TRISB12
#define SCK_DDS_DIR         TRISBbits.TRISB14
#define MOSI_DDS_DIR        TRISBbits.TRISB15
#define MISO_DDS_DIR        TRISBbits.TRISB4
#define MCLK_DDS_DIR        TRISFbits.TRISF3

#define SCK_DDS_RP          14
#define MOSI_DDS_RP         29
#define MISO_DDS_RP         28
#define MCLK_DDS_RP         16

// AD5160 digital potentiometer interface pin definitions
#define nCS_POT             LATCbits.LATC12
#define SCK_POT             PORTDbits.RD11
#define MOSI_POT            PORTDbits.RD8
#define MISO_POT            PORTBbits.RB5

#define nCS_POT_DIR         TRISCbits.TRISC12
#define SCK_POT_DIR         TRISDbits.TRISD11
#define MOSI_POT_DIR        TRISDbits.TRISD8
#define MISO_POT_DIR        TRISBbits.TRISB5

#define SCK_POT_RP          12
#define MOSI_POT_RP         2
#define MISO_POT_RP         18

// Wavegen mode pin defitions
#define nSQUARE             LATDbits.LATD6
#define WG_GAIN             LATEbits.LATE2

#define nSQUARE_DIR         TRISDbits.TRISD6
#define WG_GAIN_DIR         TRISEbits.TRISE2

// Scope channel gain pin definitions
#define CH1_GAIN            LATEbits.LATE1
#define CH2_GAIN            LATEbits.LATE0

#define CH1_GAIN_DIR        TRISEbits.TRISE1
#define CH2_GAIN_DIR        TRISEbits.TRISE0

// Peripheral remappable pin definitions
#define INT1_RP             1
#define INT2_RP             2
#define INT3_RP             3
#define INT4_RP             4

#define MOSI1_RP            7
#define SCK1OUT_RP          8
#define MOSI2_RP            10
#define SCK2OUT_RP          11

#define MISO1_RP            40
#define SCK1IN_RP           41
#define MISO2_RP            44
#define SCK2IN_RP           45

#define OC1_RP              18
#define OC2_RP              19
#define OC3_RP              20
#define OC4_RP              21
#define OC5_RP              22
#define OC6_RP              23
#define OC7_RP              24
#define OC8_RP              25
#define OC9_RP              35

#define U1TX_RP             3
#define U1RTS_RP            4
#define U2TX_RP             5
#define U2RTS_RP            6
#define U3TX_RP             28
#define U3RTS_RP            29
#define U4TX_RP             30
#define U4RTS_RP            31

#define U1RX_RP             36
#define U1CTS_RP            37
#define U2RX_RP             38
#define U2CTS_RP            39
#define U3RX_RP             35
#define U3CTS_RP            43
#define U4RX_RP             54
#define U4CTS_RP            55

// Convenience boolean values definitions
#define FALSE               0
#define TRUE                1

#define OFF                 0
#define ON                  1

#define OUT                 0
#define IN                  1

// Vendor request definitions
#define TOGGLE_LED1         0
#define TOGGLE_LED2         1
#define TOGGLE_LED3         2
#define READ_SW1            3
#define SET_DAC1            5
#define GET_DAC1            6
#define SET_DAC2            7
#define GET_DAC2            8
#define SET_DACS            9
#define GET_DACS            10
#define PULSE_MCP6N11_EN    11
#define TRIGGER             12
#define SET_PERIOD          13
#define GET_PERIOD          14
#define GET_SCOPE_BUFFER    15
#define GET_SWEEP_PROGRESS  16
#define SET_CH1_RANGE       17
#define GET_CH1_RANGE       18
#define SET_CH2_RANGE       19
#define GET_CH2_RANGE       20
#define SET_MAX_AVG         21
#define GET_MAX_AVG         22
#define GET_NUM_AVG         23
#define SET_WG_RANGE        24
#define GET_WG_RANGE        25
#define SET_NSQUARE         26
#define GET_NSQUARE         27
#define SPI_OUT_DDS         28
#define SPI_OUT_POT         29
#define SET_SHAPE_VAL       30
#define GET_SHAPE_VAL       31
#define SET_FREQ_VALS       32
#define GET_FREQ_VALS       33
#define SET_PHASE_VAL       34
#define GET_PHASE_VAL       35
#define SET_AMPLITUDE_VAL   36
#define GET_AMPLITUDE_VAL   37
#define SET_SQ_OFFSET_ADJ   38
#define GET_SQ_OFFSET_ADJ   39
#define SET_NSQ_OFFSET_ADJ  40
#define GET_NSQ_OFFSET_ADJ  41
#define READ_FLASH          42
#define WRITE_FLASH         43
#define ERASE_FLASH         44

void init_oscope(void);

#endif

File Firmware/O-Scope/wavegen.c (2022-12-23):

#include "oscope.h"
#include "wavegen.h"

uint16_t shape_val, freq_val_l, freq_val_h;
uint16_t phase_val, amplitude_val, offset_val;
uint16_t sq_offset_adj, nsq_offset_adj;
uint16_t AD9837_control_bits;

uint16_t wavegen_offset_mode, wavegen_offset_samples;
WORD32 wavegen_offset_address;

void __attribute__((interrupt, no_auto_psv)) _T3Interrupt(void) {
    IFS0bits.T3IF = 0;

    __asm__("push _TBLPAG");
    TBLPAG = wavegen_offset_address.w[1];
    DAC1DAT = __builtin_tblrdl(wavegen_offset_address.w[0]);
    __asm__("pop _TBLPAG");

    wavegen_offset_address.ul += 2;
    wavegen_offset_samples--;
    if (wavegen_offset_samples == 0) {
        if (wavegen_offset_mode) {
            wavegen_offset_address.ul = WAVEGEN_OFFSET_SAMPLE_MEM;
            __asm__("push _TBLPAG");
            TBLPAG = WAVEGEN_OFFSET_NUM_SAMPLES >> 16;
            wavegen_offset_samples = __builtin_tblrdl(WAVEGEN_OFFSET_NUM_SAMPLES & 0xFFFF);
            __asm__("pop _TBLPAG");
        } else {
            wavegen_offset_stop();
        }
    }
}

void init_wavegen(void) {
    uint8_t *RPOR, *RPINR;

    RPOR = (uint8_t *)&RPOR0;
    RPINR = (uint8_t *)&RPINR0;

    nCS_DDS_DIR = OUT; nCS_DDS = 1;
    SCK_DDS_DIR = OUT; SCK_DDS = 1;
    MOSI_DDS_DIR = OUT; MOSI_DDS_DIR = OUT;
    MCLK_DDS_DIR = OUT; MCLK_DDS = 0;

    __builtin_write_OSCCONL(OSCCON & 0xBF);
    RPINR[MISO1_RP] = MISO_DDS_RP;
    RPOR[MOSI_DDS_RP] = MOSI1_RP;
    RPOR[SCK_DDS_RP] = SCK1OUT_RP;
    __builtin_write_OSCCONL(OSCCON | 0x40);

    SPI1CON1 = 0x0172;              // SPI mode = 2, SCK freq = 1 MHz
    SPI1CON2 = 0;
    SPI1STAT = 0x8000;

    nCS_POT_DIR = OUT; nCS_POT = 1;
    SCK_POT_DIR = OUT; SCK_POT = 0;
    MOSI_POT_DIR = OUT; MOSI_POT = 0;

    __builtin_write_OSCCONL(OSCCON & 0xBF);
    RPINR[MISO2_RP] = MISO_POT_RP;
    RPOR[MOSI_POT_RP] = MOSI2_RP;
    RPOR[SCK_POT_RP] = SCK2OUT_RP;
    __builtin_write_OSCCONL(OSCCON | 0x40);

    SPI2CON1 = 0x0132;              // SPI mode = 0, SCK freq = 1 MHz
    SPI2CON2 = 0;
    SPI2STAT = 0x8000;

    __builtin_write_OSCCONL(OSCCON & 0xBF);
    RPOR[MCLK_DDS_RP] = OC5_RP;
    __builtin_write_OSCCONL(OSCCON | 0x40);

    OC5CON1 = 0x1C06;               // configure OC5 to produce a 4 MHz, 50% duty cycle PWM output
    OC5CON2 = 0x001F;
    OC5RS = 3;
    OC5R = 1;

    nSQUARE_DIR = OUT; nSQUARE = 1;
    WG_GAIN_DIR = OUT; WG_GAIN = 0;

    AD9837_control_bits = AD9837_B28 | AD9837_RESET;
    spi_out_dds(AD9837_CONTROL | AD9837_control_bits);

    sq_offset_adj = 580;
    nsq_offset_adj = 580;

    set_shape(0);                   // set initial shape to DC
    set_freq(1573, 4);              // set initial freq to 1 kHz
    set_phase(0);
    set_amplitude(0);               // set initial amplitude to 0 V
    set_offset(500);                // set initial offset to 2.5 V

    T3CON = 0x0010;                 // set Timer3 period to 30ms
    PR3 = 0xEA5F;
    TMR3 = 0;
    IFS0bits.T3IF = 0;

    wavegen_offset_set_mode(SINGLE);
    wavegen_offset_samples = 0;
    wavegen_offset_address.ul = WAVEGEN_OFFSET_SAMPLE_MEM;
}

void set_wg_gain(uint16_t value) {
    WG_GAIN = (value) ? 1 : 0;
}

uint16_t get_wg_gain(void) {
    return (WG_GAIN) ? 1 : 0;
}

void set_nsq(uint16_t value) {
    nSQUARE = (value) ? 1 : 0;
}

uint16_t get_nsq(void) {
    return (nSQUARE) ? 1 : 0;
}

void spi_out_dds(uint16_t value) {
    uint16_t ret;
    WORD temp;

    temp.w = value;
    nCS_DDS = 0;
    SPI1BUF = (uint16_t)temp.b[1];
    while (SPI1STATbits.SPIRBF == 0) {}
    ret = SPI1BUF;
    SPI1BUF = (uint16_t)temp.b[0];
    while (SPI1STATbits.SPIRBF == 0) {}
    ret = SPI1BUF;
    nCS_DDS = 1;
}

void spi_out_pot(uint8_t value) {
    uint16_t ret;

    nCS_POT = 0;
    SPI2BUF = (uint16_t)value;
    while (SPI2STATbits.SPIRBF == 0) {}
    ret = SPI2BUF;
    nCS_POT = 1;
}

void set_shape(uint16_t value) {
    if (value <= 3)
        shape_val = value;
    switch (shape_val) {
        case DC:
            AD9837_control_bits |= AD9837_RESET;
            AD9837_control_bits &= ~(AD9837_OPBITEN | AD9837_MODE | AD9837_DIV2);
            spi_out_dds(AD9837_CONTROL | AD9837_control_bits);
            nSQUARE = 1;
            DAC2DAT = nsq_offset_adj;
            break;
        case SIN:
            AD9837_control_bits &= ~(AD9837_RESET | AD9837_OPBITEN | AD9837_MODE | AD9837_DIV2);
            spi_out_dds(AD9837_CONTROL | AD9837_control_bits);
            nSQUARE = 1;
            DAC2DAT = nsq_offset_adj;
            break;
        case SQUARE:
            AD9837_control_bits |= (AD9837_OPBITEN | AD9837_DIV2);
            AD9837_control_bits &= ~(AD9837_RESET | AD9837_MODE);
            spi_out_dds(AD9837_CONTROL | AD9837_control_bits);
            nSQUARE = 0;
            DAC2DAT = sq_offset_adj;
            break;
        case TRIANGLE:
            AD9837_control_bits |= AD9837_MODE;
            AD9837_control_bits &= ~(AD9837_RESET | AD9837_OPBITEN | AD9837_DIV2);
            spi_out_dds(AD9837_CONTROL | AD9837_control_bits);
            nSQUARE = 1;
            DAC2DAT = nsq_offset_adj;
    }
}

uint16_t get_shape(void) {
    return shape_val;
}

void set_freq(uint16_t value_l, uint16_t value_h) {
    freq_val_l = value_l;
    freq_val_h = value_h;
    if ((AD9837_control_bits & AD9837_FSEL) != 0) {
        spi_out_dds(AD9837_14FREQ0 | freq_val_l);
        spi_out_dds(AD9837_14FREQ0 | freq_val_h);
        AD9837_control_bits &= ~AD9837_FSEL;
        spi_out_dds(AD9837_CONTROL | AD9837_control_bits);
    } else {
        spi_out_dds(AD9837_14FREQ1 | freq_val_l);
        spi_out_dds(AD9837_14FREQ1 | freq_val_h);
        AD9837_control_bits |= AD9837_FSEL;
        spi_out_dds(AD9837_CONTROL | AD9837_control_bits);
    }
}

uint16_t get_freq_l(void) {
    return freq_val_l;
}

uint16_t get_freq_h(void) {
    return freq_val_h;
}

void set_phase(uint16_t value) {
    phase_val = value;
    if ((AD9837_control_bits & AD9837_PSEL) != 0) {
        spi_out_dds(AD9837_12PHASE0 | (phase_val & 0x0FFF));
        AD9837_control_bits &= ~AD9837_PSEL;
        spi_out_dds(AD9837_CONTROL | AD9837_control_bits);
    } else {
        spi_out_dds(AD9837_12PHASE1 | (phase_val & 0x0FFF));
        AD9837_control_bits |= AD9837_PSEL;
        spi_out_dds(AD9837_CONTROL | AD9837_control_bits);
    }
}

uint16_t get_phase(void) {
    return phase_val;
}

void set_amplitude(uint16_t value) {
    amplitude_val = value & 0xFF;
    spi_out_pot((uint8_t)amplitude_val);
}

uint16_t get_amplitude(void) {
    return amplitude_val;
}

void set_offset(uint16_t value) {
    offset_val = value & 0x03FF;
    if (T3CONbits.TON == 0)
        DAC1DAT = offset_val;
}

uint16_t get_offset(void) {
    return offset_val;
}

void set_sq_offset_adj(uint16_t value) {
    sq_offset_adj = value & 0x03FF;
    DAC2DAT = sq_offset_adj;
}

uint16_t get_sq_offset_adj(void) {
    return sq_offset_adj;
}

void set_nsq_offset_adj(uint16_t value) {
    nsq_offset_adj = value & 0x03FF;
    DAC2DAT = nsq_offset_adj;
}

uint16_t get_nsq_offset_adj(void) {
    return nsq_offset_adj;
}

void wavegen_offset_set_interval(uint16_t value1, uint16_t value2) {
    wavegen_offset_stop();
    PR3 = value1;
    T3CON = value2;
}

void wavegen_offset_set_mode(uint16_t value) {
    wavegen_offset_mode = (value) ? REPEAT : SINGLE;
}

uint16_t wavegen_offset_get_mode(void) {
    return wavegen_offset_mode;
}

void wavegen_offset_start(void) {
    uint16_t no_samples_present;

    wavegen_offset_address.ul = WAVEGEN_OFFSET_SAMPLE_MEM;
    __asm__("push _TBLPAG");
    TBLPAG = WAVEGEN_OFFSET_NUM_SAMPLES >> 16;
    wavegen_offset_samples = __builtin_tblrdl(WAVEGEN_OFFSET_NUM_SAMPLES & 0xFFFF);
    no_samples_present = __builtin_tblrdh(WAVEGEN_OFFSET_NUM_SAMPLES & 0xFFFF);
    __asm__("pop _TBLPAG");

    if (no_samples_present)
        return;

    IFS0bits.T3IF = 0;
    TMR3 = 0;
    IEC0bits.T3IE = 1;
    T3CONbits.TON = 1;
}

void wavegen_offset_stop(void) {
    T3CONbits.TON = 0;
    IEC0bits.T3IE = 0;
    set_offset(offset_val);
}

uint16_t wavegen_offset_get_samples_left(void) {
    return wavegen_offset_samples;
}

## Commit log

2022-12-23 Initial commit.
    [3382g-001-xxx.stp, ABM10.STP, ABS06-107.STP, Analog_Devices_Inc_-_ADXL362BCCZ.step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]
2023-01-24 Fixed scope probe input resistive divider values to match current O-Scopes (i.e. 1 MΩ input resistance instead of 10 MΩ).
